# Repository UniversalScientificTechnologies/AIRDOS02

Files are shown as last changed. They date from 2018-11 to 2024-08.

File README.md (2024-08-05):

# AIRDOS02 - Airborne cosmic radiation dosimeter with GNSS receiver

Replaced with a more advanced version [AIRDOS04](https://docs.dos.ust.cz/airdos/AIRDOS04).

AIRDOS02A back panel AIRDOS front panel

Cosmic radiation dosimeter and spectrometer unit. It is intended for airborne measurement of cosmic radiation and dosimetry in mixed ionization fields on board aircraft.

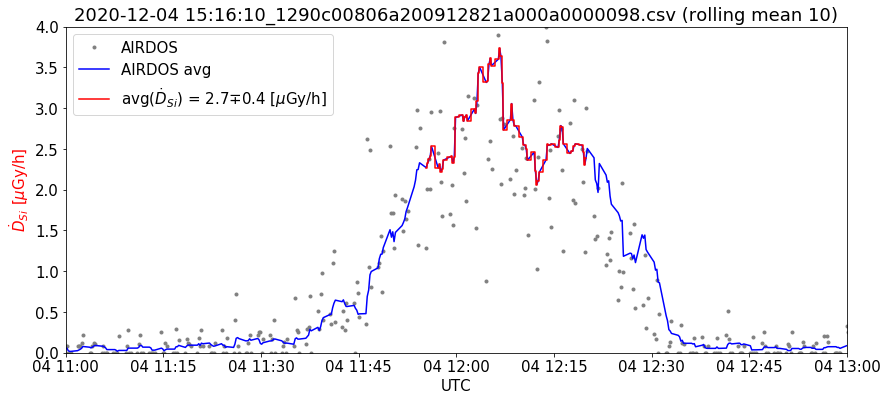
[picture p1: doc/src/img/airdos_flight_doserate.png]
AIRDOS02A flux rate measurement during aircraft flight flux rate measured by AIRDOS


### Technical parameters

* Silicon PIN diode detector with 44 mm³ detection volume
* Measurement endurance up to 200 days with two LS33600 battery cells
* Number of energy channels 248
* Energy measurement resolution <60 keV/channel
* GPS logging interval of 10 minutes or more.
* Time to GPS fix	26 s
* Airborne GPS parameters (navigation altitude verified up to 36 km a.m.s.l.)
* Radiation spectra integration time  10 s
* Size LxWxH 166 mm x 107 mm x 57 mm
* Weight 0.85 kg (Without batteries and GPS antenna)

The device can be purchased from [Universal Scientific Technologies s.r.o](http://www.ust.cz). Contact us by [email](sale@ust.cz) for a commercial quotation.

## Hardware description

### Block schematics

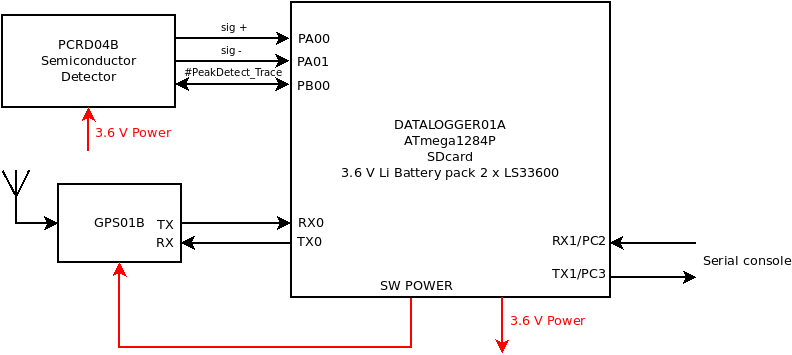
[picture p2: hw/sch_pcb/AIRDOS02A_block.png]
AIRDOS02A block diagram


#### PCRD04B - semiconductor detector circuit

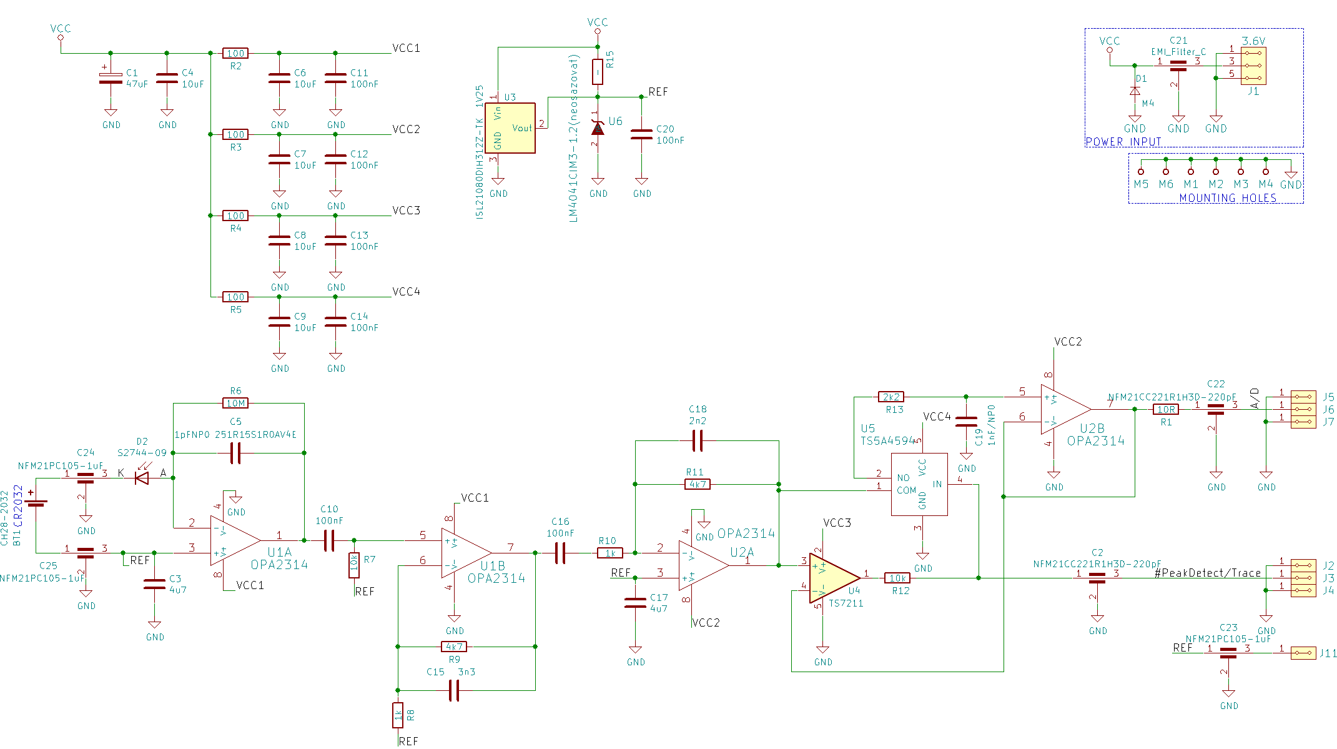
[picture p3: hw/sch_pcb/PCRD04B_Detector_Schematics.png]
AIRDOS02A - detektor schematics


### Wired connections

| DATALOGGER01A       | PCRD04B           | Color | Length |
| :-------------: |:-------------:| :-----:|:-----:|
| PB0     | TRACE | purple |10cm shield |
| GND     | POWER GND | black |10cm shield |
| VDD    | POWER VDD | orange |10cm shield |
| PA0     | A/D | yellow |10cm shield |
| PA1    | REF | grey |10cm shield |

| DATALOGGER01A       | GPS01A          | Color | Length |
| :-------------: |:-------------:| :-----:|:-----:|
| GND SWPOWER     | GND POWER | black |15cm |
| VDD SWPOWER     | VDD POWER | orange |15cm |
| TX0     | RX0 | orange |15cm |
| RX0     | TX0 | yellow |15cm |

### Jumper configuration

| GPS01B       |           |
| :-------------: |:-------------:|
| USB     | OFF |
| EXT.POWER     | EXT |
| ANT.TYPE   | Active |

| DATALOGER01A       |           |
| :-------------: |:-------------:|
| SDVDD     |  |
| POWER - BATERY     |  |

## Relevant publications

  * [AIRDOS — open-source PIN diode airborne dosimeter](https://iopscience.iop.org/article/10.1088/1748-0221/16/03/T03006)
  * [CALIBRATION OF SILICON DETECTORS LIULIN AND AIRDOS USING COSMIC RAYS AND TIMEPIX FOR USE AT FLIGHT ALTITUDES](https://doi.org/10.1093/rpd/ncac104)

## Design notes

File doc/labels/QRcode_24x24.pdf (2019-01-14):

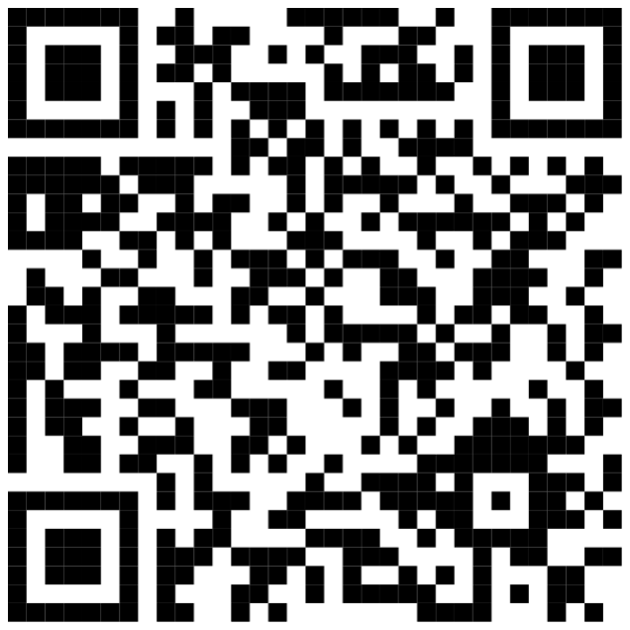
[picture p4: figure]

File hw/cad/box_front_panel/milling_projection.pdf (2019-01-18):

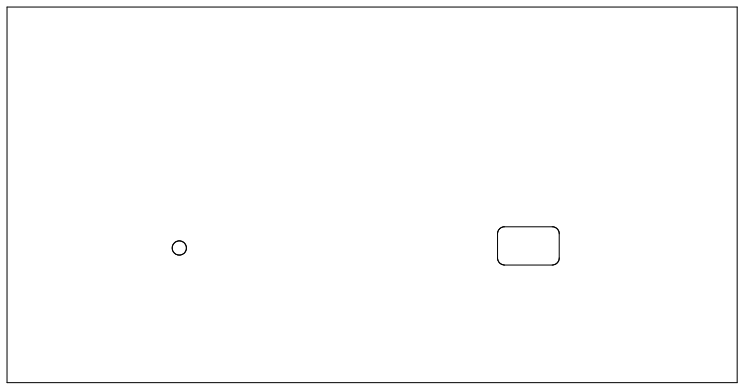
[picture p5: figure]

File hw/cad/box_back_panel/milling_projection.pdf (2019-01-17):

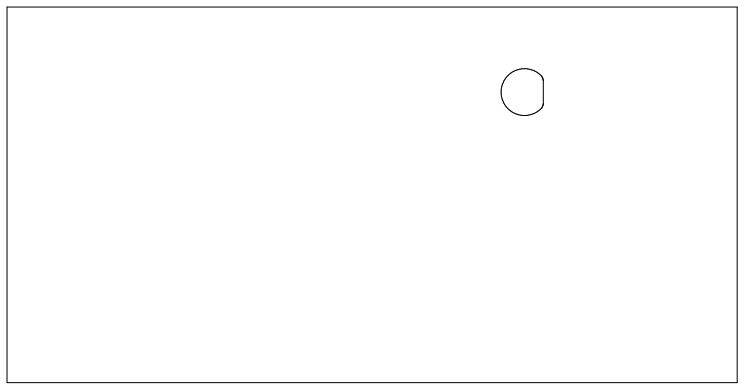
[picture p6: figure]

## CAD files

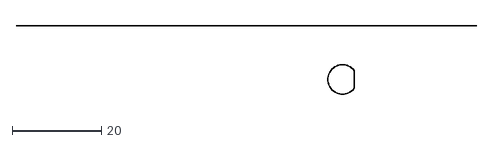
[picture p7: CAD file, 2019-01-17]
hw/cad/box_back_panel/milling_projection.dxf
103.0 x 15.3

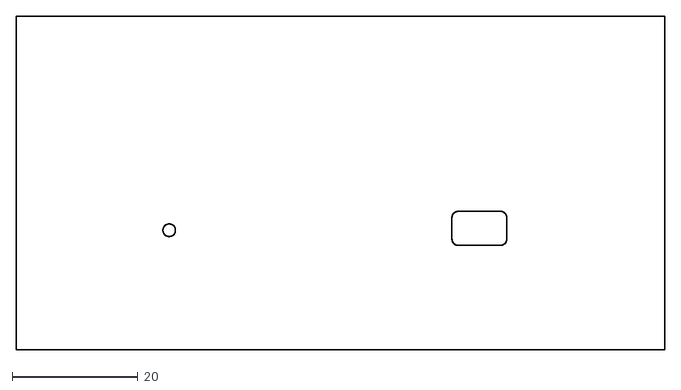
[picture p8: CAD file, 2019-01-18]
hw/cad/box_front_panel/milling_projection.dxf
103.0 x 53.0

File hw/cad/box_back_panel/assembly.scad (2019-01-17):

//CELICKO ZADNI
//---------------------------------------
$fn=100;
//PARAMETRY CELICKA OD VYROBCE
//rozměr čelíčka
celicko_x=103;
celicko_y=53;
celicko_z=1.5;

//otvory v celisku od vyrobce
celicko_dira_prumer=3.5;
celicko_dira_souradniceX=95.02/2; //souradnice od stredu celicka
celicko_dira_souradniceY=45/2;    //souradnice od stredu celicka
//---------------------------------------

//PRUMER FREZY
freza_prumer=2;

//OTVORY FREZA
//otvor_1 - pro SMA
otvor1_prumer=6.6;
otvor1_vyska=5.95; //vyska srazene hrany
otvor1_souradniceX=21.5; //souradnice od stredu celicka
otvor1_souradniceY=14.5; //souradnice od stredu celicka

//---------------------------------------

CELICKO_VYSLEDNE();

module CELICKO_VYSLEDNE(){
    difference() {
        CELICKO_OD_VYROBCE();
    
        //otvor1
        translate([otvor1_souradniceX,otvor1_souradniceY,0])  
            minkowski() {
                difference() { 
                    cylinder(celicko_z, d=otvor1_prumer-freza_prumer, center=true); 
                    translate([otvor1_vyska-freza_prumer,0,0])
                        cube([otvor1_prumer-freza_prumer,otvor1_prumer-freza_prumer,celicko_z+0.1],center=true); 
            	}  
                cylinder(r=freza_prumer/2,h=0.01, center=true);
            }  
    
    } 
} 

module CELICKO_OD_VYROBCE(){
    difference() {
        cube([celicko_x,celicko_y,celicko_z],center=true);

/*
//otvory na srouby    
translate([celicko_dira_souradniceX,celicko_dira_souradniceY,0])  
    cylinder(celicko_z+0.01, d=celicko_dira_prumer, center=true);   
     zakomentováno díry neodpovídají realitě, značná nepřesnost výrobce
translate([-celicko_dira_souradniceX,celicko_dira_souradniceY,0])  
    cylinder(celicko_z+0.01, d=celicko_dira_prumer, center=true); 

translate([celicko_dira_souradniceX,-celicko_dira_souradniceY,0])  
    cylinder(celicko_z+0.01, d=celicko_dira_prumer, center=true); 

translate([-celicko_dira_souradniceX,-celicko_dira_souradniceY,0])  
    cylinder(celicko_z+0.01, d=celicko_dira_prumer, center=true);  
   */ 
} 
} 

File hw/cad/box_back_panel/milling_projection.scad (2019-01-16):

use <assembly.scad>;

projection(cut = false) CELICKO_VYSLEDNE(); 

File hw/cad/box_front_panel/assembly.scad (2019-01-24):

//CELICKO PREDNI
//---------------------------------------
$fn=100;
//PARAMETRY CELICKA OD VYROBCE
//rozměr čelíčka
celicko_x=103;
celicko_y=53;
celicko_z=1.5;

//otvory v celisku od vyrobce
celicko_dira_prumer=3.5;
celicko_dira_souradniceX=95.02/2; //souradnice od stredu celicka
celicko_dira_souradniceY=45/2;    //souradnice od stredu celicka
//---------------------------------------

//PRUMER FREZY
freza_prumer=2;

//OTVORY FREZA
//otvor_1 - pro LED
otvor1_prumer=2;
otvor1_souradniceX=-27.2; //souradnice od stredu celicka
otvor1_souradniceY=-7.5; //souradnice od stredu celicka

//otvor_2 - pro vypinac
otvor2_rozmerX=6.7; //rozměry čisté bez úprav pro frézování
otvor2_rozmerY=5.4; //rozměry čisté bez úprav pro frézování
otvor2_souradniceX=22.05; //souradnice od stredu celicka
otvor2_souradniceY=-7.2; //souradnice od stredu celicka
//---------------------------------------

CELICKO_VYSLEDNE();

module CELICKO_VYSLEDNE(){
    difference() {
        CELICKO_OD_VYROBCE();
    
        //otvor1
        translate([otvor1_souradniceX,otvor1_souradniceY,0])  
            cylinder(h = celicko_z+0.01, d=otvor1_prumer, center=true);   

        //otvor2
        translate([otvor2_souradniceX,otvor2_souradniceY,0])  
            minkowski() {
                cube([otvor2_rozmerX, otvor2_rozmerY-freza_prumer, celicko_z], center=true);
                cylinder(d = freza_prumer,h = 0.01, center = true);
            } 
    } 
} 

module CELICKO_OD_VYROBCE(){
    difference() {
        cube([celicko_x,celicko_y,celicko_z],center=true);

/*
//otvory na srouby    
translate([celicko_dira_souradniceX,celicko_dira_souradniceY,0])  
    cylinder(celicko_z+0.01, d=celicko_dira_prumer, center=true);   
     zakomentováno díry neodpovídají realitě, značná nepřesnost výrobce
translate([-celicko_dira_souradniceX,celicko_dira_souradniceY,0])  
    cylinder(celicko_z+0.01, d=celicko_dira_prumer, center=true); 

translate([celicko_dira_souradniceX,-celicko_dira_souradniceY,0])  
    cylinder(celicko_z+0.01, d=celicko_dira_prumer, center=true); 

translate([-celicko_dira_souradniceX,-celicko_dira_souradniceY,0])  
    cylinder(celicko_z+0.01, d=celicko_dira_prumer, center=true);  
   */ 
	} 
} 



module drill_helper(){
    difference() {

        cube([celicko_x+10,celicko_y+10,celicko_z+10],center=true);

        translate([0,0,(celicko_z+10)/2 - celicko_z/2]) 
        	CELICKO_OD_VYROBCE();
    
        //otvor1
        translate([otvor1_souradniceX,otvor1_souradniceY,0])  
            cylinder(h = 30, d = 1.3, center=true);

        translate([otvor2_souradniceX,otvor2_souradniceY,0])  
            minkowski() {
                cube([otvor2_rozmerX, otvor2_rozmerY-freza_prumer, celicko_z], center=true);
                cylinder(d = freza_prumer,h = 30, center = true);
            }    
    } 
} 

translate([0,100,0])
	drill_helper();

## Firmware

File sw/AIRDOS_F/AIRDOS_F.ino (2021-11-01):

//#define DEBUG // Please comment it if you are not debugging
String githash = "f157c1d";
String FWversion = "F4";
#define ZERO 256  // 5th channel is channel 1 (column 10 from 0, ussually DCoffset or DCoffset+1)

/*
  AIRDOS with RTC (AIRDOS-F)
 
3 month endurance with LS 33600 = 7.6 mA

ISP
---
PD0     RX
PD1     TX
RESET#  through 50M capacitor to RST#

SDcard
------
DAT3   SS   4 B4
CMD    MOSI 5 B5
DAT0   MISO 6 B6
CLK    SCK  7 B7

ANALOG
------
+      A0  PA0
-      A1  PA1
RESET  0   PB0

LED
---
LED_yellow  23  PC7         // LED for Dasa


                     Mighty 1284p    
                      +---\/---+
           (D 0) PB0 1|        |40 PA0 (AI 0 / D24)
           (D 1) PB1 2|        |39 PA1 (AI 1 / D25)
      INT2 (D 2) PB2 3|        |38 PA2 (AI 2 / D26)
       PWM (D 3) PB3 4|        |37 PA3 (AI 3 / D27)
    PWM/SS (D 4) PB4 5|        |36 PA4 (AI 4 / D28)
      MOSI (D 5) PB5 6|        |35 PA5 (AI 5 / D29)
  PWM/MISO (D 6) PB6 7|        |34 PA6 (AI 6 / D30)
   PWM/SCK (D 7) PB7 8|        |33 PA7 (AI 7 / D31)
                 RST 9|        |32 AREF
                VCC 10|        |31 GND
                GND 11|        |30 AVCC
              XTAL2 12|        |29 PC7 (D 23)
              XTAL1 13|        |28 PC6 (D 22)
      RX0 (D 8) PD0 14|        |27 PC5 (D 21) TDI
      TX0 (D 9) PD1 15|        |26 PC4 (D 20) TDO
RX1/INT0 (D 10) PD2 16|        |25 PC3 (D 19) TMS
TX1/INT1 (D 11) PD3 17|        |24 PC2 (D 18) TCK
     PWM (D 12) PD4 18|        |23 PC1 (D 17) SDA
     PWM (D 13) PD5 19|        |22 PC0 (D 16) SCL
     PWM (D 14) PD6 20|        |21 PD7 (D 15) PWM
                      +--------+
*/

/*
// Compiled with: Arduino 1.8.9
// MightyCore 2.0.2 https://mcudude.github.io/MightyCore/package_MCUdude_MightyCore_index.json
Fix old bug in Mighty SD library
~/.arduino15/packages/MightyCore/hardware/avr/2.0.2/libraries/SD/src/SD.cpp:
boolean SDClass::begin(uint32_t clock, uint8_t csPin) {
  if(root.isOpen()) root.close();
*/

#include <SD.h>             // Revised version from MightyCore
#include "wiring_private.h"
#include <Wire.h>           
#include "src/RTCx/RTCx.h"  // Modified version included

#define LED_yellow  23   // PC7
#define RESET       0    // PB0
#define SDpower1    1    // PB1
#define SDpower2    2    // PB2
#define SDpower3    3    // PB3
#define SS          4    // PB4
#define MOSI        5    // PB5
#define MISO        6    // PB6
#define SCK         7    // PB7
#define INT         20   // PC4

#define CHANNELS 512 // number of channels in buffer for histogram, including negative numbers

uint16_t count = 0;
uint32_t serialhash = 0;
uint16_t offset;
uint16_t base_offset = ZERO - 1;
uint8_t lo, hi;
uint16_t u_sensor, maximum;
struct RTCx::tm tm;

// Read Analog Differential without gain (read datashet of ATMega1280 and ATMega2560 for refference)
// Use analogReadDiff(NUM)
//   NUM  | POS PIN             | NEG PIN           |   GAIN
//  0 | A0      | A1      | 1x
//  1 | A1      | A1      | 1x
//  2 | A2      | A1      | 1x
//  3 | A3      | A1      | 1x
//  4 | A4      | A1      | 1x
//  5 | A5      | A1      | 1x
//  6 | A6      | A1      | 1x
//  7 | A7      | A1      | 1x
//  8 | A8      | A9      | 1x
//  9 | A9      | A9      | 1x
//  10  | A10     | A9      | 1x
//  11  | A11     | A9      | 1x
//  12  | A12     | A9      | 1x
//  13  | A13     | A9      | 1x
//  14  | A14     | A9      | 1x
//  15  | A15     | A9      | 1x
#define PIN 0
uint8_t analog_reference = INTERNAL2V56; // DEFAULT, INTERNAL, INTERNAL1V1, INTERNAL2V56, or EXTERNAL

void setup()
{

  // Open serial communications and wait for port to open:
  Serial.begin(9600);

  Serial.println("#Cvak...");
  
  ADMUX = (analog_reference << 6) | ((PIN | 0x10) & 0x1F);
  
  ADCSRB = 0;               // Switching ADC to Free Running mode
  sbi(ADCSRA, ADATE);       // ADC autotrigger enable (mandatory for free running mode)
  sbi(ADCSRA, ADSC);        // ADC start the first conversions
  sbi(ADCSRA, 2);           // 0x100 = clock divided by 16, 62.5 kHz, 208 us for 13 cycles of one AD conversion, 24 us fo 1.5 cycle for sample-hold
  cbi(ADCSRA, 1);        
  cbi(ADCSRA, 0);        

  pinMode(RESET, OUTPUT);   // reset for peak detetor

  //pinMode(SDpower1, OUTPUT);  // SDcard interface
  //pinMode(SDpower2, OUTPUT);     
  //pinMode(SDpower3, OUTPUT);     
  //pinMode(SS, OUTPUT);     
  //pinMode(MOSI, INPUT);     
  //pinMode(MISO, INPUT);     
  //pinMode(SCK, OUTPUT);  

  DDRB = 0b10011110;
  PORTB = 0b00000000;  // SDcard Power OFF

  DDRA = 0b11111100;
  PORTA = 0b00000000;  // SDcard Power OFF
  DDRC = 0b11101100;
  PORTC = 0b00000000;  // SDcard Power OFF
  DDRD = 0b11111100;
  PORTD = 0b00000000;  // SDcard Power OFF

  pinMode(LED_yellow, OUTPUT);
  digitalWrite(LED_yellow, LOW);  
  digitalWrite(RESET, LOW);  
  
  //!!! Wire.setClock(100000);

  for(int i=0; i<5; i++)  
  {
    delay(50);
    digitalWrite(LED_yellow, HIGH);  // Blink for Dasa 
    delay(50);
    digitalWrite(LED_yellow, LOW);  
  }

  Serial.println("#Hmmm...");

  // make a string for device identification output
  String dataString = "$AIRDOS," + FWversion + "," + String(ZERO) + "," + githash + ","; // FW version and Git hash
  
  Wire.beginTransmission(0x58);                   // request SN from EEPROM
  Wire.write((int)0x08); // MSB
  Wire.write((int)0x00); // LSB
  Wire.endTransmission();
  Wire.requestFrom((uint8_t)0x58, (uint8_t)16);    
  for (int8_t reg=0; reg<16; reg++)
  { 
    uint8_t serialbyte = Wire.read(); // receive a byte
    if (serialbyte<0x10) dataString += "0";
    dataString += String(serialbyte,HEX);    
    serialhash += serialbyte;
  }

  {
    DDRB = 0b10111110;
    PORTB = 0b00001111;  // SDcard Power ON
  
    // make sure that the default chip select pin is set to output
    // see if the card is present and can be initialized:
    if (!SD.begin(SS)) 
    {
      Serial.println("#Card failed, or not present");
      // don't do anything more:
      return;
    }
  
    // open the file. note that only one file can be open at a time,
    // so you have to close this one before opening another.
    File dataFile = SD.open("datalog.txt", FILE_WRITE);
  
    // if the file is available, write to it:
    if (dataFile) 
    {
      dataFile.println(dataString);  // write to SDcard (800 ms)     
      dataFile.close();
  
      digitalWrite(LED_yellow, HIGH);  // Blink for Dasa
      Serial.println(dataString);  // print SN to terminal 
      digitalWrite(LED_yellow, LOW);          
    }  
    // if the file isn't open, pop up an error:
    else 
    {
      Serial.println("#error opening datalog.txt");
    }
  
    DDRB = 0b10011110;
    PORTB = 0b00000001;  // SDcard Power OFF          
  }    

  // measurement of ADC offset
  ADMUX = (analog_reference << 6) | 0b10001; // Select +A1,-A1 for offset correction
  delay(200);
  ADCSRB = 0;               // Switching ADC to Free Running mode
  sbi(ADCSRA, ADATE);       // ADC autotrigger enable (mandatory for free running mode)
  sbi(ADCSRA, ADSC);        // ADC start the first conversions
  sbi(ADCSRA, 2);           // 0x100 = clock divided by 16, 62.5 kHz, 208 us for 13 cycles of one AD conversion, 24 us fo 1.5 cycle for sample-hold
  cbi(ADCSRA, 1);
  cbi(ADCSRA, 0);
  sbi(ADCSRA, ADIF);                  // reset interrupt flag from ADC
  while (bit_is_clear(ADCSRA, ADIF)); // wait for the first conversion
  sbi(ADCSRA, ADIF);                  // reset interrupt flag from ADC
  lo = ADCL;
  hi = ADCH;
  ADMUX = (analog_reference << 6) | 0b10000; // Select +A0,-A1 for measurement
  ADCSRB = 0;               // Switching ADC to Free Running mode
  sbi(ADCSRA, ADATE);       // ADC autotrigger enable (mandatory for free running mode)
  sbi(ADCSRA, ADSC);        // ADC start the first conversions
  sbi(ADCSRA, 2);           // 0x100 = clock divided by 16, 62.5 kHz, 208 us for 13 cycles of one AD conversion, 24 us fo 1.5 cycle for sample-hold
  cbi(ADCSRA, 1);
  cbi(ADCSRA, 0);
  // combine the two bytes
  u_sensor = (hi << 7) | (lo >> 1);
  // manage negative values
  if (u_sensor <= (CHANNELS / 2) - 1 ) {
    u_sensor += (CHANNELS / 2);
  } else {
    u_sensor -= (CHANNELS / 2);
  }

  // Initiates RTC
  rtc.autoprobe();
  rtc.resetClock();
}
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

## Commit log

2019-01-16 box front panel
    [assembly.scad]
2019-01-16 New projection view for generating a milling data.
    [milling_projection.dxf, milling_projection.scad]
2019-01-17 Box panel
    [assembly.scad, milling_projection.dxf, milling_projection.scad]
2019-01-17 Codestyle update.
    [assembly.scad]
2019-01-18 Edit front panel
    [assembly.scad, milling_projection.dxf]
2019-01-24 Drilling helper created.
    [assembly.scad]
2021-12-29 AIRDOS F with temperature and pressure sensor
2023-09-01 Update README.md
    Fix PIN diode detection volume.
